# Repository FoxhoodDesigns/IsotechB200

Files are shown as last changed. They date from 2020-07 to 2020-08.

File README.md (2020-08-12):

# IsotechB200

This github contains the source files of the Amsterdam University of Applied Science innovationlab assignment: B-200 ADC substitution.

With the data in this repository one can recreate the design made for the project and utilize this as a Jump-off point for further development.

# CODE
Contains a sample code showing how to use the Interface with a digital Microcontroller. In this case a regular Arduino UNO.

# EAGLE
Contains Autodesk Eagle board files. Which includes circuit schematic and PCB design.

Note: For possible Eagle library dependancies please view this repository: https://github.com/FoxhoodDesigns/FHD-Libraries

# LTSPICE
Contains the LTSPICE Simulation file used for simulating the analog component of the Interface board

# doc
Contains the PDF and source LaTeX files behind the research. For documentation referencing purposes.

All work presently contained within this repository is made by the original AUAS team:
Chiel Voswijk, Kwint van den Berg and Niels Hupkens.

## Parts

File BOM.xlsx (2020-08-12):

BOM | B-200 ADC Substitution
Part | Type | Brand | Model | Price | Supplier | link
U1 | Multiplexer | Various | DG406DJ | 11.45 | Farnell | https://nl.farnell.com/maxim-integrated-products/dg406dj/analogue-mux-demux-single-16-1/dp/2513882?st=DG406
U2 | Connector | Various | DB-25 |  | Farnell
U3 | ADC | Microchip | MCP3201 | 2.15 | Farnell | https://nl.farnell.com/microchip/mcp3201-ci-p/ic-adc-12bit-100ksps-pdip-8/dp/9758577?st=MCP3201
U4 | DC-DC Generator | Tracopower | TMR 1-0522 | 12.49 | Conrad | https://www.conrad.nl/p/tracopower-tmr-1-0522-dcdc-converter-print-5-vdc-12-vdc-12-vdc-42-ma-1-w-aantal-uitgangen-2-x-1510835
IC1 | Op-Amp | Various | NE5532 | 0.794 | Farnell | https://nl.farnell.com/texas-instruments/ne5532ap/op-amp-dual-low-noise-5532-dip8/dp/1106091?st=NE5532
IC2 | Op-Amp | Various | NE5532 | 0.794 | Farnell | https://nl.farnell.com/texas-instruments/ne5532ap/op-amp-dual-low-noise-5532-dip8/dp/1106091?st=NE5532
R1 | 0207 Resistor | Generic | 10K | 0.03 | Farnell | https://nl.farnell.com/multicomp/mf12-10k/res-10k-1-125mw-axial-metal-film/dp/9342419
R2 | 0207 Resistor | Generic | 3K | 0.03 | Farnell | https://nl.farnell.com/multicomp/mf12-3k/res-3k-1-125mw-axial-metal-film/dp/9342990
R3 | 0207 Resistor | Generic | 10K | 0.03 | Farnell | https://nl.farnell.com/multicomp/mf12-10k/res-10k-1-125mw-axial-metal-film/dp/9342419
R4 | 0207 Resistor | Generic | 10K | 0.03 | Farnell | https://nl.farnell.com/multicomp/mf12-10k/res-10k-1-125mw-axial-metal-film/dp/9342419
R5 | Precision-Potentiometer | Generic | 10K | 2.16 | Farnell | https://nl.farnell.com/bourns/3296w-1-103lf/pot-trimmer-10k-25turn-10/dp/9353186?st=otentiometer%2010k
C1 | 1206 Ceramic capacitor | Generic | 100nf | 0.01 | Farnell | https://nl.farnell.com/kemet/c1206c104k5rac7210/cap-0-1-f-50v-10-x7r-1206/dp/2905763?st=1206%20100nf
C2 | 1206 Ceramic capacitor | Generic | 1n | 0.02 | Farnell | https://nl.farnell.com/kemet/c1206c102k5ractu/cap-1000pf-50v-10-x7r-1206-reel/dp/2392384?st=1206%201nf
C3 | 1206 Ceramic capacitor | Generic | 100nf | 0.01 | Farnell | https://nl.farnell.com/kemet/c1206c104k5rac7210/cap-0-1-f-50v-10-x7r-1206/dp/2905763?st=1206%20100nf
C4 | 2,5mm spaced Capacitor | Generic | 10u | 0.213 | Farnell | https://nl.farnell.com/rubycon/50ms510mefc6-3x5/cap-10-f-50v-20/dp/1144604?st=10uf%20capacitor
J1 | Male Headers | Generic | 10*2 |  | Farnell

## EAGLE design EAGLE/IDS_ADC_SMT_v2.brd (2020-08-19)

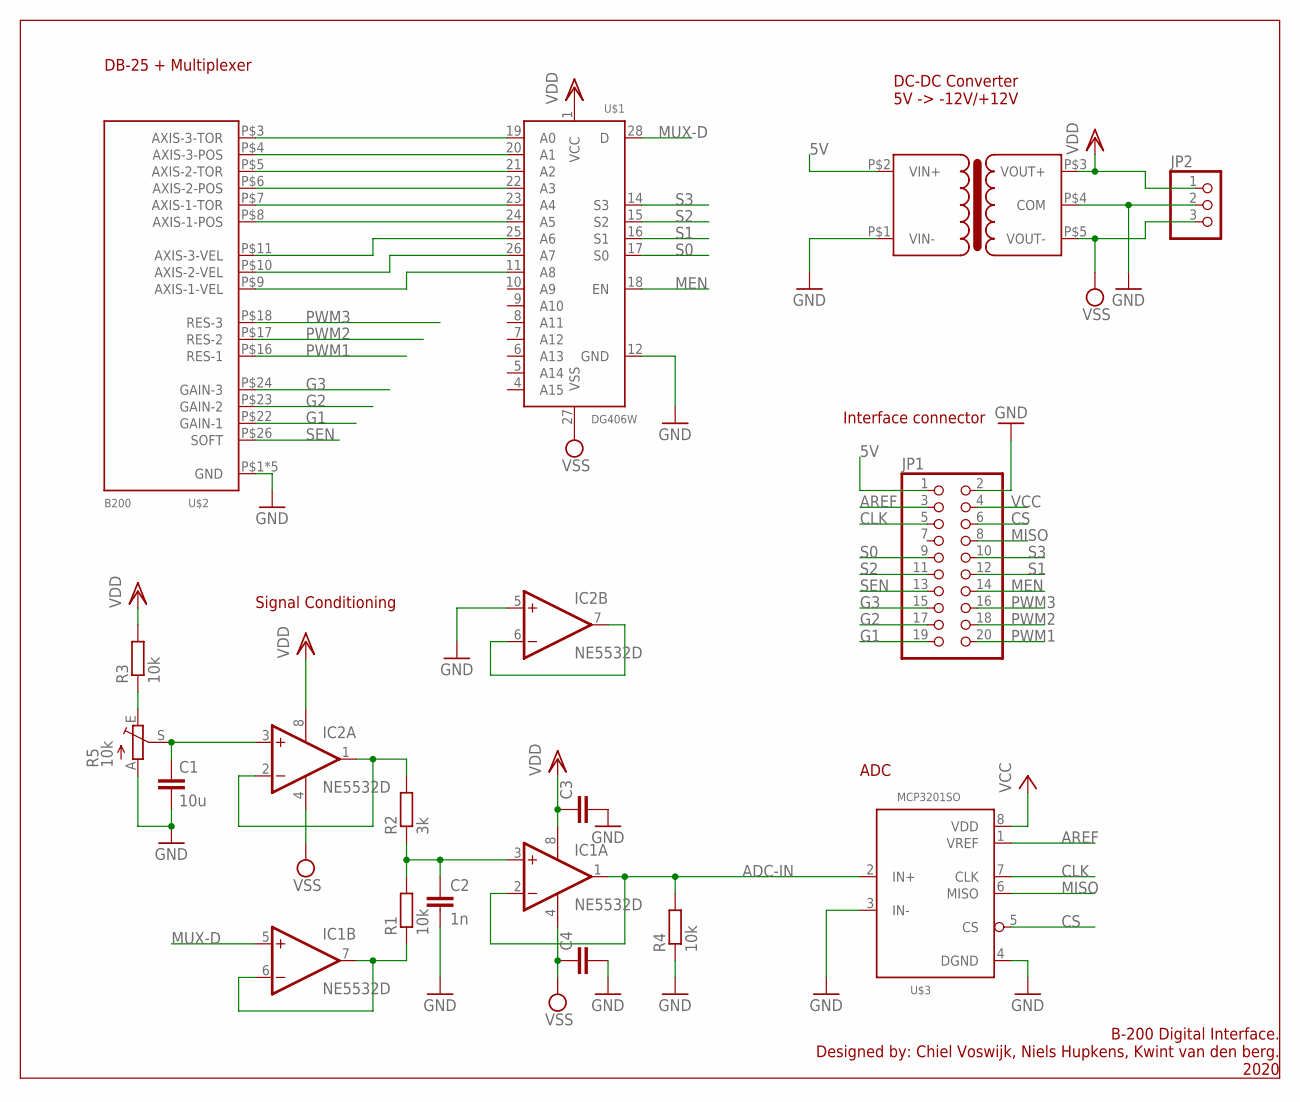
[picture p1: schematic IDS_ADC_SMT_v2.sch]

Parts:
C1: 10u; C1210
C2: 1n; C0805
C3, C4: C-EUC0805; C0805
IC1, IC2: NE5532D; SO08
JP1: PINHD-2X10; 2X10
JP2: PINHD-1X3; 1X03
R1, R3, R4: 10k; R0805
R2: 3k; R0805
R5: 10k; RJ9W
U$1: DG406W; SO-28W
U$2: B200; PARALLEL
U$3: MCP3201SO; SO-8
U$4: TRACO-DR-NE; TRACO-DCDC-SIP6

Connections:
5V: JP1.1, U$4.P$2 (VIN+)
ADC-IN: IC1.1 (OUT), IC1.2 (-IN), R4.2, U$3.2 (IN+)
AREF: JP1.3, U$3.1 (VREF)
CLK: JP1.5, U$3.7 (CLK)
CS: JP1.6, U$3.5 (CS)
G1: JP1.19, U$2.P$22 (GAIN-1)
G2: JP1.17, U$2.P$23 (GAIN-2)
G3: JP1.15, U$2.P$24 (GAIN-3)
GND: C1.2, C2.2, C3.2, C4.2, IC2.5 (+IN), JP1.2, JP2.2, R4.1, R5.A, U$1.12 (GND), U$2.P$1 (GND), U$2.P$2 (GND), U$2.P$19 (GND), U$2.P$20 (GND), U$2.P$21 (GND), U$3.3 (IN-), U$3.4 (DGND), U$4.P$1 (VIN-), U$4.P$4 (COM)
MEN: JP1.14, U$1.18 (EN)
MISO: JP1.8, U$3.6 (MISO)
MUX-D: IC1.5 (+IN), U$1.28 (D)
unnamed: IC2.6 (-IN), IC2.7 (OUT)
unnamed: U$1.19 (A0), U$2.P$3 (AXIS-3-TOR)
unnamed: C2.1, IC1.3 (+IN), R1.2, R2.1
unnamed: U$1.20 (A1), U$2.P$4 (AXIS-3-POS)
unnamed: IC1.6 (-IN), IC1.7 (OUT), R1.1
unnamed: U$1.21 (A2), U$2.P$5 (AXIS-2-TOR)
unnamed: IC2.1 (OUT), IC2.2 (-IN), R2.2
unnamed: C1.1, IC2.3 (+IN), R5.S
unnamed: U$1.22 (A3), U$2.P$6 (AXIS-2-POS)
unnamed: U$1.23 (A4), U$2.P$7 (AXIS-1-TOR)
unnamed: U$1.24 (A5), U$2.P$8 (AXIS-1-POS)
unnamed: U$1.25 (A6), U$2.P$11 (AXIS-3-VEL)
unnamed: U$1.26 (A7), U$2.P$10 (AXIS-2-VEL)
unnamed: U$1.11 (A8), U$2.P$9 (AXIS-1-VEL)
unnamed: R3.1, R5.E
PWM1: JP1.20, U$2.P$16 (RES-1)
PWM2: JP1.18, U$2.P$17 (RES-2)
PWM3: JP1.16, U$2.P$18 (RES-3)
S0: JP1.9, U$1.17 (S0)
S1: JP1.12, U$1.16 (S1)
S2: JP1.11, U$1.15 (S2)
S3: JP1.10, U$1.14 (S3)
SEN: JP1.13, U$2.P$26 (SOFT)
VCC: JP1.4, U$3.8 (VDD)
VDD: C3.1, IC1.8 (V+), IC2.8 (V+), JP2.1, R3.2, U$1.1 (VCC), U$4.P$3 (VOUT+)
VSS: C4.1, IC1.4 (V-), IC2.4 (V-), JP2.3, U$1.27 (VSS), U$4.P$5 (VOUT-)

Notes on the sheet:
DB-25 + Multiplexer
DC-DC Converter 5V -> -12V/+12V
ADC
Signal Conditioning
Interface connector
B-200 Digital Interface. Designed by: Chiel Voswijk, Niels Hupkens, Kwint van den berg. 2020

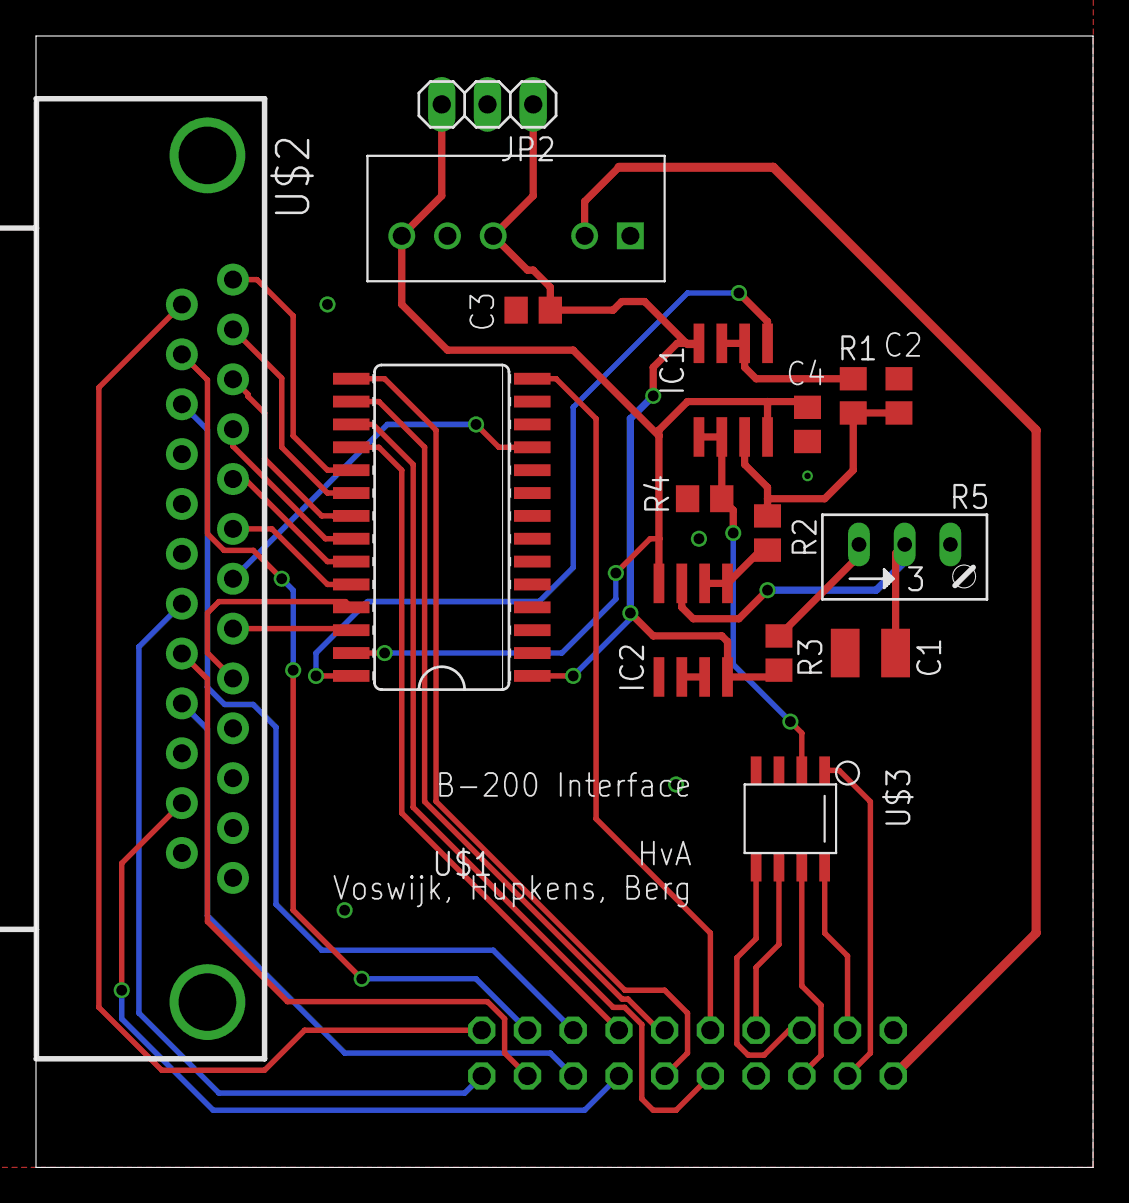
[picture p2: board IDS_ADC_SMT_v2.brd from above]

Board: 2 copper layers, 58.7 x 62.9 mm, 17 parts (1 on the bottom side), 38 nets.

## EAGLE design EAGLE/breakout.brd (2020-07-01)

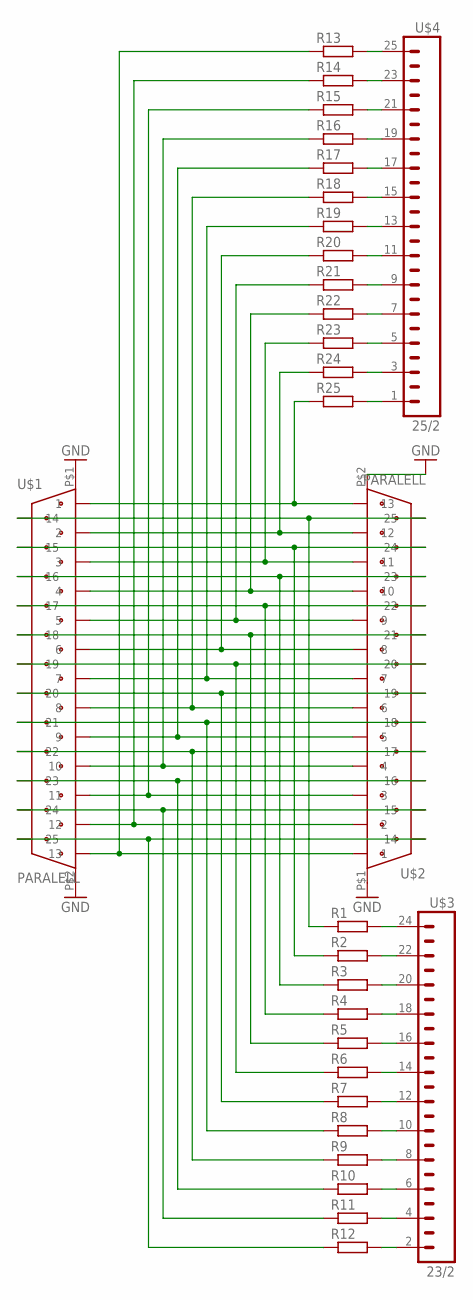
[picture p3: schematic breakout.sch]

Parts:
R1, R2, R3, R4, R5, R6, R7, R8, R9, R10, R11, R12, R13, R14, R15, R16, R17, R18, R19, R20, R21, R22, R23, R24, R25: R-EU_0204/7; 0204/7
U$1, U$2: PARALELL; PARALLEL
U$3: 23/2; 1X23
U$4: 25/2; 1X25

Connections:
GND: U$1.P$1, U$1.P$2, U$2.P$1, U$2.P$2
unnamed: R13.1, U$1.P$15 (13), U$2.P$3 (1)
unnamed: R14.1, U$1.P$14 (12), U$2.P$4 (2)
unnamed: R15.1, U$1.P$13 (11), U$2.P$5 (3)
unnamed: R16.1, U$1.P$12 (10), U$2.P$6 (4)
unnamed: R17.1, U$1.P$11 (9), U$2.P$7 (5)
unnamed: R18.1, U$1.P$10 (8), U$2.P$8 (6)
unnamed: R19.1, U$1.P$9 (7), U$2.P$9 (7)
unnamed: R20.1, U$1.P$8 (6), U$2.P$10 (8)
unnamed: R21.1, U$1.P$7 (5), U$2.P$11 (9)
unnamed: R22.1, U$1.P$6 (4), U$2.P$12 (10)
unnamed: R23.1, U$1.P$5 (3), U$2.P$13 (11)
unnamed: R24.1, U$1.P$4 (2), U$2.P$14 (12)
unnamed: R25.1, U$1.P$3 (1), U$2.P$15 (13)
unnamed: R1.2, U$3.24
unnamed: R2.2, U$3.22
unnamed: R3.2, U$3.20
unnamed: R4.2, U$3.18
unnamed: R5.2, U$3.16
unnamed: R6.2, U$3.14
unnamed: R7.2, U$3.12
unnamed: R8.2, U$3.10
unnamed: R9.2, U$3.8
unnamed: R10.2, U$3.6
unnamed: R11.2, U$3.4
unnamed: R12.2, U$3.2
unnamed: R13.2, U$4.25
unnamed: R14.2, U$4.23
unnamed: R15.2, U$4.21
unnamed: R16.2, U$4.19
unnamed: R17.2, U$4.17
unnamed: R18.2, U$4.15
unnamed: R19.2, U$4.13
unnamed: R20.2, U$4.11
unnamed: R21.2, U$4.9
unnamed: R22.2, U$4.7
unnamed: R23.2, U$4.5
unnamed: R24.2, U$4.3
unnamed: R25.2, U$4.1
unnamed: R1.1, U$1.P$16 (14), U$2.P$27 (25)
unnamed: R2.1, U$1.P$17 (15), U$2.P$26 (24)
unnamed: R3.1, U$1.P$18 (16), U$2.P$25 (23)
unnamed: R4.1, U$1.P$19 (17), U$2.P$24 (22)
unnamed: R5.1, U$1.P$20 (18), U$2.P$23 (21)
unnamed: R6.1, U$1.P$21 (19), U$2.P$22 (20)
unnamed: R7.1, U$1.P$22 (20), U$2.P$21 (19)
unnamed: R8.1, U$1.P$23 (21), U$2.P$20 (18)
unnamed: R9.1, U$1.P$24 (22), U$2.P$19 (17)
unnamed: R10.1, U$1.P$25 (23), U$2.P$18 (16)
unnamed: R11.1, U$1.P$26 (24), U$2.P$17 (15)
unnamed: R12.1, U$1.P$27 (25), U$2.P$16 (14)

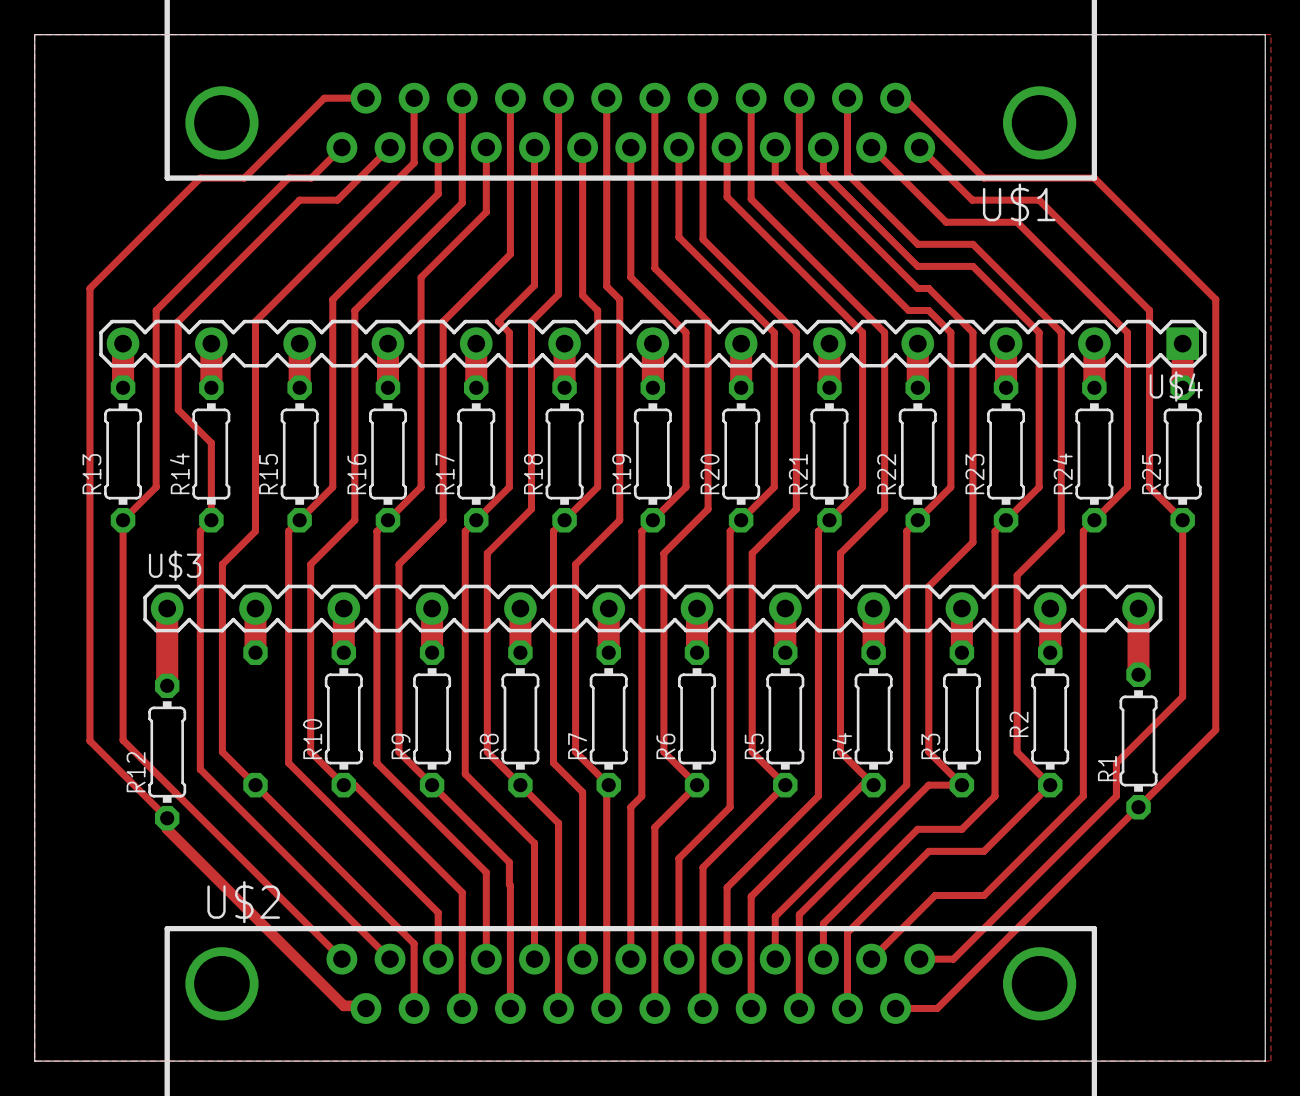
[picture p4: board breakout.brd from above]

Board: 2 copper layers, 70.8 x 59.0 mm, 29 parts (1 on the bottom side), 51 nets.

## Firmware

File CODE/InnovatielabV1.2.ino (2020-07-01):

//InovatieLab Arduino ADC demonstratie Code
//Geschreven: Kwint van den Berg. 2020

#include <SPI.h>
#include <SD.h>
File myFile;

// MCP3102
#define DAT  12  // SPI MISO Pin
#define CLK  13  // SPI Clock Pin
#define CS   8   // SPI SS Pin (Chip Select)

// ADG406 Multiplexer pins 
#define PIN_MULPLEX_EN A2
#define PIN_MULPLEX_S0 7
#define PIN_MULPLEX_S1 A1
#define PIN_MULPLEX_S2 A3
#define PIN_MULPLEX_S3 A0

//Weerstand PWM pins
#define PIN_PWM1    3
#define PIN_PWM2    5
#define PIN_PWM3    6

//Weerstand GAIN pins
#define PIN_GAIN1   A5
#define PIN_GAIN2   A4
#define PIN_STATE   2

//Analog Reference voltage in Millivolts (5000 for Arduino 5V, 3300 for 3.3V or any own value if using external Reference generation. 
#define ADCREF   5000

//________________________________________________________Configuration________________________________________________________________

#define PRINT  0      // text = 1 plot = 0
#define SHOWCHANNELS  0x01FF        // 0x0000 .. 0x01FF


#define PWM1  10     // 1..100 % Weerstand
#define PWM2  10     // 1..100 % Weerstand
#define PWM3  10     // 1..100 % Weerstand

#define GAIN1  LOW    // 0 of 1
#define GAIN2  LOW    // 0 of 1
#define STATE  1      // 0 of 1   0 = manual 1 = Software 

//___________________________________________________________________________________________________________________________________

void setup()
{
  int val;
  Serial.begin(115200);

  //Check if SD present, Else do not continue
  if (PRINT) Serial.print("Initializing SD card...");
  if (!SD.begin(4))
  {
    if (PRINT) Serial.println("initialization failed!");
    while (1);
  }
  if (PRINT) Serial.println(" initialization done.");

  
  myFile = SD.open("output.csv", FILE_WRITE); // Generate File
  if (myFile)
  {
    if (PRINT) Serial.print("Writing to: output.csv");
    delay(250);
  }
  else
  {
    // if the file didn't open, print an error:
    if (PRINT) Serial.println("error opening output.csv");
  }

   //Intialize SPI bus for ADC
  SPI.beginTransaction(SPISettings(1500000, MSBFIRST, SPI_MODE0));
  SPI.begin();

  pinMode(DAT, INPUT);
  pinMode(CS, OUTPUT);

  digitalWrite(CS, LOW);  // Cycle CS pin to ensure PWR ON state is high.
  digitalWrite(CS, HIGH);
  digitalWrite(CLK, LOW);  // Turn clck low

  //Define Multiplexer outputs as such.
  pinMode(PIN_MULPLEX_EN, OUTPUT);      // sets the digital pin  as output
  pinMode(PIN_MULPLEX_S0, OUTPUT);      // sets the digital pin  as output
  pinMode(PIN_MULPLEX_S1, OUTPUT);      // sets the digital pin  as output
  pinMode(PIN_MULPLEX_S2, OUTPUT);      // sets the digital pin  as output
  pinMode(PIN_MULPLEX_S3, OUTPUT);      // sets the digital pin  as output

  setMultiplexer(0);                    // Set multiplex to 0

  // set PWM (remaps percentage to 8-bit value)
  val = map(PWM1, 0, 100, 0, 255);
  analogWrite(PIN_PWM1, val);
  val = map(PWM2, 0, 100, 0, 255);
  analogWrite(PIN_PWM2, val);
  val = map(PWM3, 0, 100, 0, 255);
  analogWrite(PIN_PWM3, val);

  // setting state and gain
  pinMode(PIN_GAIN1, OUTPUT);
  pinMode(PIN_GAIN2, OUTPUT);
  pinMode(PIN_STATE, OUTPUT);
  digitalWrite(PIN_GAIN1, GAIN1);
  digitalWrite(PIN_GAIN2, GAIN2);
  digitalWrite(PIN_STATE, STATE);
}

//Sets all relevant output pins for multiplexer according to address given
void setMultiplexer(byte input)
{
  digitalWrite(PIN_MULPLEX_EN, 0);  // Disable
  delayMicroseconds(1);

  digitalWrite(PIN_MULPLEX_S0, input & 0x01);  // sets the S0
  digitalWrite(PIN_MULPLEX_S1, input & 0x02);  // sets the S0
  digitalWrite(PIN_MULPLEX_S2, input & 0x04);  // sets the S0
  digitalWrite(PIN_MULPLEX_S3, input & 0x08);  // sets the S0

  digitalWrite(PIN_MULPLEX_EN, 1);  //  Enable
  delayMicroseconds(10);
}

float readoutMP3201(void)
{
  unsigned int reading = 0;      // To be measured reading

  digitalWrite(CS, LOW);         //Select MCP3102 for reading
  reading = SPI.transfer16(0x0000); // Copy latest reading from ADC
  digitalWrite(CS, HIGH);        //Unselect MCP3102

  //Trim the received 16 bits to gain 12-bit value. The top 3 MSB and the bottom LSB are not of interest.
  reading = reading << 3;   //Remove the top 3 MSB (unused) by shifting upwards
  reading = reading >> 4;   //Shift back down plus an extra in order to remove the lowest bit. Leaving the actual value

  //Convert reading into a Voltage (for displaying)
  float voltage = reading * (5.000 / ADCREF); // Using.
  //Return Voltage
  return (voltage);
}

void loop()
{
  float measure;
  char buf[50];
  int cnt;
  unsigned long currentMillis = millis();
  int channel;

  //Write current time to File
  myFile.print(currentMillis);
  myFile.print("\t");
  if (PRINT)
  {
    Serial.print(currentMillis);
    Serial.print("\t");
  }
  //Go through each analog channel, Writing the measurement to SD and to Terminal.
  for (cnt = 0, channel = 0x0001; cnt < 9; cnt++, channel = channel << 1)
  {
    setMultiplexer(cnt);

    measure = readoutMP3201();

    myFile.print(measure, 3);
    myFile.print("\t");

    if (SHOWCHANNELS & channel)
    {
      Serial.print(measure, 3);
      Serial.print("\t");
    }
  }

  myFile.print("\n");
  myFile.flush();
  Serial.print("\n");
  //If a new number is received. Update all PWM for demonstration:
  byte new_pwm;
  if (Serial.available()) {
    //Read the new value
    new_pwm = Serial.read();
    //Remap from percentage to byte
    new_pwm = map(new_pwm, 0, 100, 0, 255);
    analogWrite(PIN_PWM1, new_pwm);
    analogWrite(PIN_PWM2, new_pwm);
    analogWrite(PIN_PWM3, new_pwm);
  }
  
}

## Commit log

2020-07-01 Initial Upload Source Material
    [IDS_ADC.brd, IDS_ADC.sch, breakout.brd, breakout.sch]
2020-08-19 SMT Version Upload
    Uploaded a largely SMT design for future production.
    NOTE: Parallel port is still reversed. Pending future update.
    [IDS_ADC_SMT.brd, IDS_ADC_SMT.sch]
2020-08-19 SMT Final
    Fully corrected, optimized and miniaturized SMT version of the Interface board.
    [IDS_ADC_SMT_v2.brd, IDS_ADC_SMT_v2.sch]
